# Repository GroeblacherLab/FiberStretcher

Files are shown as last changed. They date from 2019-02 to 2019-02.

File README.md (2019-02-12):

# FiberStretcher
3D-printed optical fiber stretcher for phase control of light. It can be used, for example, to lock the phase between two arms of an interferometer.

Example of an older version:

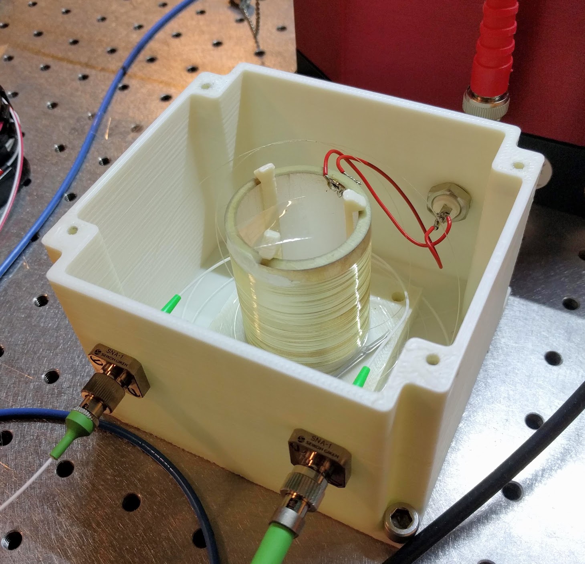
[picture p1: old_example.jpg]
example of an older version


## Required equipment

* Tube piezoelectric actuator [such as this one](https://www.steminc.com/PZT/en/piezo-ceramic-cylinder-40x33x50mm-32-khz). Its diameter should be large enough to reduce bending losses to an acceptable level and its fundamental resonance frequency should be chosen in accordance to the desired bandwidth of the specific application where it will be used.
* Coated optical fiber such as [SMF28](https://www.corning.com/media/worldwide/coc/documents/Fiber/SMF-28%20Ultra.pdf) (no buffer layer or jacket) 
* Fiber mating sleeve ([example](https://www.thorlabs.com/thorproduct.cfm?partnumber=ADAFC3))
* Fiber patch cord
* Fiber splicer
* BNC connector
* Super glue
* Tape
* M3, M2 screws

## Instructions

* Hold down the starting end with tape. Leave enough length at the start so you can later splice it. Also, leave enough space on the cylinder so you can later solder electrical wires to it. 
* Wind the fiber around the piezo cylinder. Keep the fiber tense around the cyllinder. See below for the number of required turns. Tape down the fiber, at the end.
* Glue down both fiber ends. Once it is dry, remove the tape.
* Splice the fiber to patch cords
* Solder the leads of the BNC connector to the inner and outer electrodes. Twist the wires to reduce interference.
* Print the three .stl files. The piezo can be mounted around the holder. The holder is screwed to the box and the lid can later be used to close the box with screws as well. You should be able to screw directly into the plastic.
* Mount the BNC and mating sleeves to the box. Connect the fiber ends to the mating sleeves. You can screw the box down to an optical breadboard.

The higher the number of windings around the cyllinder, the lower the Vpi (required voltage for a pi phase shift) will be. The number of turns N for a chosen Vpi can be calculated from N = lambda/(4 pi n d33 Vpi), where lambda is the wavelength, n is the fiber's refractive index, and d33 is the the piezoelectric constant which relates the cyllinder radial change per voltage difference. 

For more information check J. P. Moura, Making light jump: photonic crystals in trampoline membranes for optomechanics experiments, PhD Thesis, Delft University of Technology (2019)

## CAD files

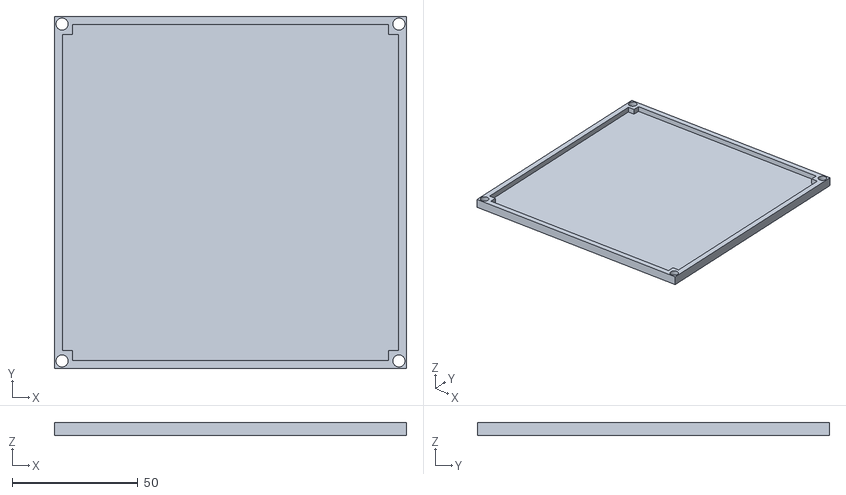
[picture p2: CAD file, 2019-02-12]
cover.STL
140.0 x 140.0 x 5.00

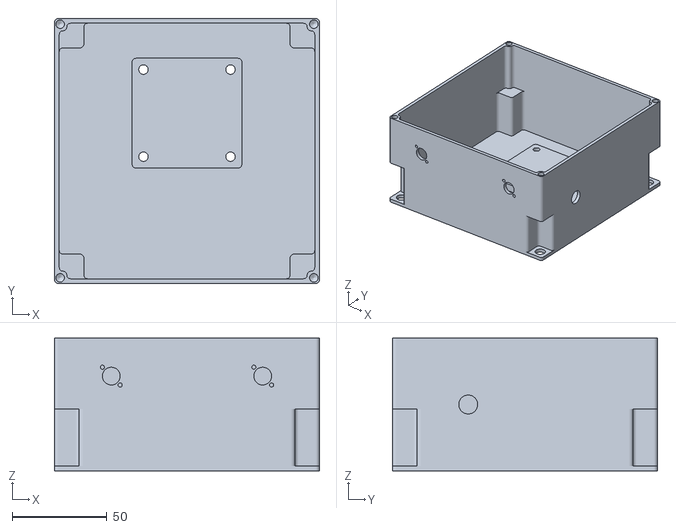
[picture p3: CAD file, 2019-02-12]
box.STL
140.0 x 140.0 x 70.0

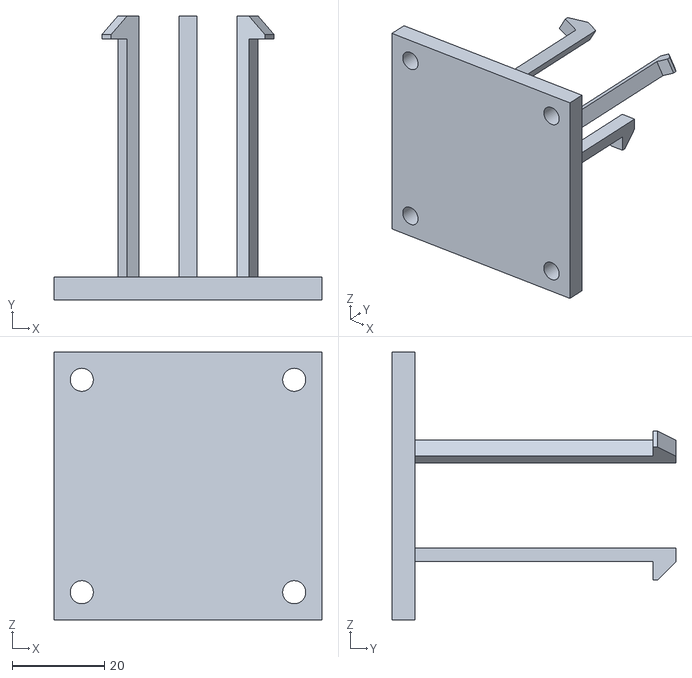
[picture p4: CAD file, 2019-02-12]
holder.STL
58.0 x 61.5 x 58.0
